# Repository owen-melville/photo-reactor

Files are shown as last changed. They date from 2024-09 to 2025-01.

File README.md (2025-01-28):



<b><h1>Overview:</b></h1>
This repository contains the instructions/code/files for the assembly and operation of the LEDbyXample photoreactor. LEDbyXample is designed for automation and self-driving labs (SDLs), like those at the Acceleration Consortium in Toronto. Although it is designed for 8 mL (2 dram) vials that can be placed inside by a robotic arm with gripper, the 3d-printed design files are easily altered for use with larger vials. Most components, including for the LEDs (~1W to be suitable for photochemistry) are modular and easy to swap.

<b><h2>Authors:</b></h2>

Owen Alfred Melville, Staff Scientist <br>
Monique Ngan, Automation Technician <br>
Jeffrey Watchorn, Staff Scientist <br>
[Acceleration Consortium](https://acceleration.utoronto.ca/) <br>
Last Updated 2024-10-22 <br>

<b><h2>Why LEDbyXample? </b></h2>
<b> Low Cost: </b> Existing photoreactors on the market are quite expensive. One of the cheapest, the [Pioreactor](https://pioreactor.com/en-ca/products/pioreactor-20ml?variant=46984254554168), costs about $340 USD ($460 CAD). There is no need for such a large price. The main parts for the LEDbyXample photoreactor cost about $80 USD, with additional electronic components from kits costing another $80 USD. Many of these additional parts are small electronic components that users may already have, and the kits provide more parts than are required by the reactor. Many of the components could also likely be sourced for cheaper as long as the builders are able to perform their own quality control checks. 

<b> Automation Friendly: </b> LEDbyXample is designed to work with automation and self-driving labs. Vials can be release inside the reactor by a robotic arm with a gripper. Automation of the stirring rpm and LED intensity is controlled through a custom python script and uses a Raspberry Pi Pico which can be commanded through a USB cable. Wireless support for the Pico is available but not documented in this project. 

<b> Skill Development: </b> LEDbyXample is made largely from scratch. This allows builders to develop their DIY skills (3D printing, electronics prototyping, microcontroller use). It contains clear build instructions with photos, links to videos, and clear part lists with links. The Python code used to communicate with the microcontroller is designed to be clear and easily modified. 

<b> Modular / Customizable: </b> LEDbyXample is designed to be modular, with components (LEDs, fans, bases) that can be easily removed or swapped. The 3D printed parts that comprise the physical reactor can be modified to accomodate for different vial sizes. 

<b><h2>Summary of Steps:</b></h2>
  1. Order the required items
  2. 3D Print the required parts
  3. Assemble the photo-reactor
  4. Operate the photo-reactor

<b><h2>Tools Required For This Project:</b></h2>
- [Soldering Iron (for electrical connections)](https://www.amazon.ca/Weller-Soldering-Station-WLACCBSH-02-Silicone/dp/B08MC4HVTR?th=1)
- [Heat Gun (for heat-shrink electrical connections)](https://www.amazon.ca/Mini-Heat-Shrink-Gun-Dual-Temp-dp-B09TYM45BH/dp/B09TYM45BH/ref=dp_ob_title_hi)
- [Wire cutters](https://www.amazon.ca/BOOSDEN-Crafting-Spring-Loaded-Plastics-Clippers/dp/B08ZCHYGN7/?th=1)
- [3D printer](https://ca.store.bambulab.com/products/p1s?srsltid=AfmBOorLX7Ki2ZaYaFx6AWRBcr8wJq_0mTlmHkm-IWXz0sfFRXeNtMNX)

<b><h2>Skills required For This Project: </b></h2>
- Soldering
- Basic Python coding

<b><h1>Step 1: Order the Required Items: </b></h1>

The majority of the components for this project are electronic. 

<b><h2>Materials Required:</b></h2>

These materials are required for the photoreactor. You would need to purchase more to make additional photoreactors. Note, only 1x Fan and 1x Fan Board are strictly needed for stirring. The active cooling Fan and Fan Board are optional. The total cost with 2 LED modules and 1 active cooling (fan) module is $82.80 USD. 

| Item                             | Supplier | Part number                   |Number | Cost (USD) | Total Cost (USD) |
| -------------------------------- | -------- | ----------------------------- | ---------------------------------------------------------------------------------------------------------------------------------------------------------------------------------------------------------------------------------------------------------------------------------------------------------------------------------------------------------------------------------------------------------------------------------------------------------------------------------------------------- | ------ | ----- |
| [Raspberry Pi Pico WH](https://www.pishop.ca/product/raspberry-pi-pico-wh-pre-soldered-headers/  )            | PiShop   | 402-1               |           1      | 9.8   | 9.8        |
| [Grove Shield for Pico](https://www.digikey.ca/en/products/detail/seeed-technology-co-ltd/103100142/13688265?s=N4IgTCBcDaIIwFYCcB2AtHADAZi5uALGGgHIAiIAugL5A)            | Digikey  | 1597-103100142-ND              | 1      | 6.25  | 6.25       |
| [Fan Control Board](https://www.digikey.ca/en/products/detail/adafruit-industries-llc/4808/13590573?s=N4IgTCBcDaIIwFYwA4C0AWZAGNA5AIiALoC%2BQA )               | Digikey  | 1528-4808-ND                   | 2      | 7.99  | 15.98      |
| [Square Fan (20mm Diameter)](https://www.digikey.ca/en/products/detail/cui-devices/CFM-2006CF-060-078-22/19524716?s=N4IgTCBcDa5mBmAtAYQGIFkkAIwAY8A2dJIvHPAdgA4l4kA5AERAF0BfIA)       | Digikey  | 2223-CFM-2006CF-060-078-22-ND |  2      | 11.06 | 22.12      |
| [Grove to Fan Board Connectors](https://www.digikey.ca/en/products/detail/adafruit-industries-llc/4528/11627737?s=N4IgTCBcDaIIwFYwA4C0AWJaByAREAugL5A)   | Digikey  | 1528-4528-ND                  | 2      | 2.83  | 5.66       |
| [Power Barrel Connector](https://www.digikey.ca/en/products/detail/same-sky-formerly-cui-devices/PJ-102AH/408448)     | Digikey  | PJ-102AH                  |  1      | 1.02  | 1.02       |
| [Power Supply](https://www.digikey.ca/en/products/detail/tri-mag-llc/L6R06H-050/7682614)    | Digikey  | L6R06H-050           |  1      | 5.31  | 5.31       |
| [LED Stars (Green)](https://www.digikey.ca/en/products/detail/new-energy/LST1-01H06-GRN1-01/10663110?s=N4IgTCBcDaIDIGUAqBGAtABhQCQwNjQHEAlAOXSxAF0BfIA)               | Digikey  | LST1-01H06-GRN1-01            |  2      | 6.41  | 12.82      |
| [NPN Transistor](https://www.digikey.ca/en/products/detail/nexperia-usa-inc/PZT2222A-115/1158011?s=N4IgTCBcDaIIwHYwILQBYwFYwrigBAHIAiIAugL5A )                  | Digikey  | 1727-4252-1-ND                |  2      | 0.56  | 1.12       |
| [USB Cable for Pico](https://www.digikey.com/en/products/detail/cvilux-usa/DH-20M50056/13177301) |  Digikey | DH-20M50056 | 1 | 2.72 | 2.72 |
| Total Cost (USD) | | | | | <b> $82.80 </b> |
| Total Cost (CAD) | | | | |<b> $115.53 </b> |

<b><h2>Materials Required - Kits:</b></h2>

These materials come in kits, so you may not need them if you already have similar materials. They can be used for multiple reactors or other projects. 

| Item                             | Supplier |  Cost (CAD) |
| -------------------------------- | -------- |  ----- |
| [Prototype PCB Board](https://www.amazon.ca/BOJACK-6-Prototype-Soldering-Compatible-Arduino/dp/B091PZQ4W7/    )              | Amazon Canada        | 21.99 |
| [Nyodenium Magnets 6mm x 2mm](https://www.amazon.ca/Magnets-Refrigertor-Whiteboard-Durable-Multi-Use/dp/B07BJFD6FL/)      | Amazon Canada     | 9.99  |
| [Heat Sinks](https://www.amazon.ca/Awxlumv-Heatsink-25-x25-x10/dp/B08CMK8BMT/ )                       | Amazon Canada   |  10.99 |
| [Resistors](https://www.amazon.ca/Resistor-Assorted-Resistors-Assortment-Experiments/dp/B07L851T3V/?th=1 )                        | Amazon Canada   | 17.99 |
| [Solder Seal Connectors](https://www.amazon.ca/Kuject-Connectors-Waterproof-Electrical-Automotive/dp/B073RMRCC3/) | Amazon Canada   | 16.99 |
| [4-Pin Connectors](https://www.amazon.ca/1-25mm-Connectors-Pre-Crimped-Pixhawk-Silicone/dp/B07S18D3RN/ )  | Amazon Canada           | 21.99 |
| [2-Pin Connectors](https://www.amazon.ca/dp/B00T2U76V0/ref=olp-opf-redir?aod=1&th=1) | Amazon Canada | 10.77 |
| Total Cost (USD) | | <b> $79.29  </b>| 
| Total Cost (CAD) | | <b> $110.71 </b> |

<b><h2>Generic Materials Required</b></h2>
  - Wires (at least red, black, blue, and yellow)
  - Solder
  - Filament for 3D printing (eg [PLA](https://ca.store.bambulab.com/products/pla-basic-filament?gad_source=1&gclid=Cj0KCQjwpP63BhDYARIsAOQkATYc5jM-nciSOOw8pbxHA_WIkh3n5OJYfMMvQm4q8-BjsxyQY5-RIlQaAhdqEALw_wcB) and [ASA](https://ca.store.bambulab.com/products/asa-filament?srsltid=AfmBOor0TaklWc8wcPPxX6YhTCeVZ4l1UiV82qqBd3xhd9iYvP6Alb0c))

<b><h2>Photo of Materials </b></h2>
 <br>

<b><h1>Step 2: 3D Print the Parts: </b></h1>

All the 3D printed parts can be printed with 0.2 mm layer height and a 0.4 mm nozzle. For prototyping or low-temperature reactors, PLA filament can be used. For higher temperatures or shorter wavelength (blue,violet,UV), ASA can be used. Since ASA tends to warp, I recommend using glue stick on the print bed. 

| File Name          | Purpose                  | Printing Considerations      | Number Required         | Customization Potential                 |
| ------------------ | ------------------------ | ---------------------------- | ----------------------- | --------------------------------------- |
| LED_holder.stl     | Holds LED + Heat Sink    | None                         | 1 per LED               |                                         |
| blank_holder.stl   | Blocks Window            | None                         | 1 per unblocked window  |                                         |
| fan_base.stl       | Holds Fan + Magnets      | Tree Supports from base only | 1                       | Change inset for larger fan             |
| fan_holder.stl     | Holds Cooling Fan        | Tree supports from base only | Only if cooling desired |                                         |
| reactor_shield.stl | Holds Vial               | Tree supports from base only | 1                       | Change circle diameter for larger vial  |
| screw_base.stl     | Connects reactor to base | None                         | 1                       | Change screw pattern for different base |



<b><h1>Step 3: Assemble the Photoreactor: </b></h1>

The 3D printed parts are modular. When assembled, they should look like this:



<b><h2> Step 3a: Assemble the LED Holders </b></h2>

The LED Holder takes the 3D printed insert, and adds in a heat sink and a ~1W LED with attached wires to be controlled by the microcontroller. 

<b>Parts Required:</b>
- LED star
- Wires
- 2-Pin Connectors (or alternative)
- 3D Printed LED Holder
- Solder seal connectors
- Heat sinks

<b>Steps:</b>
  1. Take your LED star, it should have two large soldering pads labelled + and -


 
  2. Clean the LED star pads using rubbing alcohol (isopropanol) and a tissue
  3. ***Tricky step Alert*** Attach a red wire to the + labelled pad on the right of the star, and tape it down away from the pad to keep it in place. Heat up your soldering iron in a well ventilated area, then place it over the wire. Using your non-dominant hand, feed solder to the pad from different directions, allowing it to flow onto the pad. Once the solder has covered the whole pad, carefully remove the soldering iron and replace it in its holder. The wire should be encased in solder that has made a strong bind with the pad. If after 2 minutes, gentle pressure on the solder pushes it off the pad, you may need to clean the pad and repeat the process. For tips on this process, see this video (Time Stamp 4:30) https://www.youtube.com/watch?v=H-82av4zQKY&ab_channel=MrTroutDT

https://github.com/user-attachments/assets/7bd34561-cb51-4cb3-8f49-8e8b69328b1f

  4. Repeat the last process using a black wire and the - labelled pad on the right of the star. Ensure the contact has been well made after completion


 
  5. Remove the adhesive from the heat sink, and slide it into the 3D printed LED holder. Note that the spikes of the heat sink point outwards, towards the thinner side. The flat side of the heat sink should point inwards towards the thinner side.
     


  6. Carefully feed the red and black wire through the hole at the bottom of the LED holder. If your wires will not fit, you can use a sharp knife to cut open the channel. As you feed the wires through, you may need to bend them so you can position the LED in a central location on the heat sink.


 
  7. If you wanted a permanent setup, you could wire these red and black ends straight to your LED board (Step 3c). However, to make them removable/swappable, the wires need connectors. I recommend getting a set of pre-wired connectors with red and black wires at the non-connector end. Take the red wire from your LED and the red wire from the connector, and place them in a solder seal connector so that the bare ends of the wires are touching and under the "solder" of the connector. Use your heat gun to carefully heat up the solder seal connector from different angles. First the plastic will melt, sealing the wires together, then you will see the solder spreading from the central area, which should create a proper connection between the two wires. Let the connection cool. To check that the wiring has been made correctly, you can use a multimeter, comparing the LED pad to the appropriate pin in the connector. Use this youtube video for guidance: https://www.youtube.com/watch?v=bvDk3HzS7lM&ab_channel=SkillBuilder


  
  8. Repeat the last step to connect the black wires.

<i>Congratulations, you have created your LED holder, which can slide in and out of the photoreactor! You can create as many of these as you have LEDs that you want to use </i>


 
<b><h2> Step 3b: Assemble the Fan Base </b></h2>

The fan base holds a fan with magnets to allow for magnetic stirring.

<b>Parts Required:</b>
- 3D Printed Fan Base
- Fan
- Wires
- Super glue / double-sided tape
- Magnets (x2)
- 4-Pin Connectors (or alternative)

<b>Steps:</b>
  1. Thread the wires through the hole near the center of the fan base, with the black side of the fan facing up.



  2. Carefully pull on the wires and wiggle the fan into the center square.



  3. Using super glue or double-sided tape, carefully place the magnets on the top of the fan.



  4. <b>Attach the connectors:</b> You can wire the fan to a 4-pin connector using the optional kit or an alternative. 
  
  <i>Using Optional Kit:</i> Using the same technique as in Step 3a - 7, use solder seal connectors to extend the length of the fan wires by attaching them to pre-crimped wires from the electrical connector kit. Then, connect each wire to the connector head. When inserted correctly, the ends of the wire should be fully contained inside the plastic connectors, and fit snugly in place.



  <i>Using Other Connectors:</i> If you have a pre-wired connector with 4 wire leads, you can use that instead of the connector kit. Using the same technique as in Step 3a - 7, use solder seal connectors to connect the fan wires to your pre-wired 4-pin connector. 



<i>Congratulations, you have created your Fan Base which is used to stir a magnetic rod in the reactor </i>

<b><h2> Step 3c: (Optional) Assemble the Fan Holder </b></h2>

The fan holder holds a fan to actively cool the reactor vial. The cooling capacity of the current setup is unknown, and it is possible a larger or a stronger fan is required. This will be investigated for future versions of the photoreactor. 

<b>Parts Required:</b>
- 3D Printed Fan Holder
- Fan
- Wires
- 4-Pin Connectors (or alternative)

<b>Steps:</b>
  1. Thread the wires through the hole near the bottom of the fan holder, with the black side of the fan facing out.



  2. Carefully pull on the wires and pull the fan into its slot.



  3. Using the same technique as in Step 3a - 7, use solder seal connectors to extend the length of the fan wires by attaching them to pre-crimped wires, then carefully insert the pre-crimped wires into the connector head. Alternatively, if you have a pre-wired connector with 4 wire leads, you can use that instead.



<i>Congratulations, you have created your Fan Holder which is used to cool the reactor </i>

<b><h2> Step 3d: Assemble the LED Board </b></h2>

The LED Board uses transistors to control the on/off status of the LEDs, with the signal to the transistor coming from the Rasperry pi. It also has a power inlet port to power the LEDs separately from the Pi, as they draw quite a bit of current. In the future, an LED board could be purchased to directly control the LED, including its intensity, something not currently possible with this design. The design described here controls 2 LEDs at a time, but it could be extended to control more LEDs at once. 

<b>Parts Required:</b>
- PCB board from Kit (60x40 mm)
- Wires
- 1x 1000 Ohm resistor
- 2x 5.6 Ohm resistor
- 2x 390 Ohm resistor
- 2x NPN Transistors
- 4-Pin Connectors (or alternative)
- 2-Pin Connectors (or alternative)
- 1x Power Barrel Connector

<b>Steps:</b>



  1. Mount the power board and solder in a 1000 Ohm resistor between the power and ground sides. This creates a power port. The GND side represents your ground, and 5V your high voltage.
  2. Solder the circuit diagram above. For now, leave the open circles with text labels. The power supply and 1000 Ohm resistor are already completed in step 1. For the NPN transistors, the drawing below shows the schematic. Pin 1 (base) goes to the 330 Ohm resistor, and eventually to the RPi GPIO Pin. This acts like a switch for this LED. Pin 2 (collector) goes towards the LED and the power supply. Pin 3 (emitter) goes to ground.



  3. Solder wires into the open circles that connect to the RPi GPIO pins. The other end of the wire can be bare or an open pin. We will connect these to the RPi in a later step.
  4. Solder wires into the open circles that connect to the LED. For clarity, you can use red wires to go towards the power supply, and black wires towards the transistors. These wires should be at their other end connected to the complementary connectors that you used in Steps 3a-7 and 3a-8. These are meant to connect and disconnect the LED holders so you can change them.
  5. Solder a black wire from the ground/- terminal. The other end of the wire can be bare or an open pin. We will connect this wire to the RPi Ground Pin in a later step, to ensure a common ground.
  

  
  6. (Optional): To add more LED outputs, add more of this section of the circuit diagram, connected in the same way. If you add many more LEDs, you may require a power supply that is rated for higher current. 



<i>Congratulations, you have created your LED Board which is used to control the reactor LEDs</i>

<b><h2> Step 3e: Assemble the Fan Board </b></h2>

The Fan Board uses pre-made fan control boards to control the RPM of the fans. It connects to the Rasperry pi and to a separate power supply. The current design is for 2 fans (1 cooling, 1 stirring) but could be easily be extended for use with more fans. 

<b>Parts Required:</b>
- PCB board (60x40 mm)
- Wires
- 1x 1000 Ohm resistor
- 2x Fan Control Board
- 2x Grove to Fan Board Connectors
- 1x Power Barrel Connector (Optional)

<b>Steps:</b>



  1a. (Optional) Mount the power board and solder in a 1000 Ohm resistor between the power and ground sides. This creates a power port. The GND side represents your ground, and 5V your high voltage.
  1b. Alternatively, you can connect the 5V using a wire to the 5V section of the LED board or to the 5V Pin in the Pico. This means one less power supply, but will draw power either from the LED power supply or from the Pico (which you don't want to draw too much from). 
  2. Solder the circuit diagram above. Solder wires into the open circles for the fan power (red) and ground (black). These will go to the 4-pin connector to the fan.
  3. For each Fan Control Board, solder wires into the "FAN" (blue) and "TACH" (yellow) ports, the other ends will go to the 4-pin connector to the fan.
  4. For each Fan Control Board, attach a Grove to Fan Board Connector. This will connect to the RPi.
  5. Take the power (red), ground (black), tach (yellow), and fan (blue) wires and connect them to a 4-pin connector that complements the one you created for your fans in step 3b-4. 



<i>Congratulations, you have created your Fan Board which is used to control the reactor Fans</i>

<b><h2> Step 3f: Combine the Electronics </b></h2>

We need to connect the boards to the raspberry pi, which controls them. Optionally, you can choose to house them in the 3D printed holder, the parts of which you would need to print. This housing is only to keep the electronics tidy, and is not needed. 

<b>Parts Required:</b>
- Assembled Fan Board (Step 3e)
- Assembled LED Board (Step 3d)
- Raspberry Pi Pico WH
- Grove Shield for Pico
- USB Cable for Pico (USB-A to micro-USB)
- Power Supply (for LED Board)
- (Optional): Power Supply (for Fan Board)
- (Optional): 3D Printed electronics housing

<b>Steps:</b>
  1. Place the Raspberry Pi into the Grove Shield. This requires some force so that it goes in all the way.
  2. Common ground: Take the wires directed towards "RPi Ground" from the Fan and LED Boards and connect them to any open pin on the Raspberry Pi Pico labelled GND.
  3. Signal wires (LEDs): Take the wires directed towards "RPi GPIO Pin 0" and "RPi GPIO Pin 1" from the LED board and connect them to the Raspberry Pi Pico in the corresponding Pins ("GP0" and "GP1")
  4. Signal wires (Fans): Take the Grove-to-stemma connectors from the fan boards and connect them to the top-right corner slots on the Raspberry Pi Pico (with the USB connector oriented up).

 <br>

<b> Optional: Add the electronics to a housing </b>

The electronics housing can be used to house the Raspberry Pi Pico and auxillary electronics. The holders for the auxillary electronics will fit the 60x40 mm PCB boards. They can be printed according to the instructions below. For the material you can use PLA but the snapping mechanism on the snap lid may work better with PETG. 

| File Name                            | Purpose                     | Printing Considerations | Number Required | Customization Potential                  |
| ------------------------------------ | --------------------------- | ----------------------- | --------------- | ---------------------------------------- |
| Pico Holder_MainBody.stl             | Holds the Pico              | Flat side down          | 1               |                                          |
| Pico Holder_Main_Lid.stl             | Lid for Main Unit           | Flat side down          | 1               |                                          |
| Aux_Module.stl                       | Holds LED/Fan Board         | Flat side down          | 2               | Could change to hold different sized PCB |
| Pico Holder_Port_Door_Default.stl    | Blank door for Aux Unit     | Flat side down          | 0               | Can add ports                            |
| Pico Holder_Port_Door_Open_Ports.stl | Custom door for Aux Unit    | Flat side down          | 2               |                                          |
| Pico_Aux_Lid_Snap.stl                | Lid for Aux Unit            | Flat side down          | 2               |                                          |
| Pico Holder_Port_Door_Honeycomb      | Honeycomb door for Aux Unit | Flat side down          | 2               |                                          |

Instructions:
- Print the pieces for the housing
- Place the boards in their respective holders with any connecting wires detached
  
 <br>

- Thread any connecting wires through the honeycomb in the sides
- Attach the side pieces and lids

 <br>

<i> Congratulations, you have finished assembling the electronics! </i>

<b><h2> Step 3g: Assemble the Reactor </b></h2>

<b>Parts Required:</b>
  - Assembled Electronics (Step 3f)
  - Assembled Fan Base (Step 3b)
  - Assembled LED Holder (Step 3a)
  - Assembled Fan Holder (Optional, Step 3c)
  - Reactor Shield
  - Blank Holders (for open unfilled slots)
  - Screw Base (Optional)

<b>Steps:</b>
  1. Connect the electrical connectors for each LED and fan to the electrical setup.

 <br>

  2. Assemble the reactor parts. The LED holder, blank holders, and fan holders should slot easily into the 4 slots on the sides of the reactor shield. The reactor shield slots onto the fan base, which slots onto the screw base. The screw base has slots for fastening the base of the reactor. These could be modified to attach the reactor to a different base or with different screws.

 </br>

<i> Congratulations, you have fully assembled the LEDbyXAmple photoreactor! </i>

<b><h1>Step 4: Operate the Photoreactor: </b></h1>

To operate the photoreactor, we will need to use a Python script that connects to the RPi Pico. The script can be used to control the RPM of the fan (with some constraints) and to turn the LEDs on and off as needed. 

<b><h2> Step 4a: Installations </b></h2>

<b>Steps:</b>
  1. Install a code editor, we recommend VSCode. 
  2. Install Python on your computer if it is not already installed.
  3. Install Micropico extension in VScode
  4. Connect the RPi Pico to your computer using the Usb B Micro B to Usb A Cable, while pressing the BOOTSEL button on the Pico. A file directory for the Pico should show up in your file explorer.
  5. Flash the Raspberry Pi  by downloading the [MicroPython UF2 file for Pico W](https://www.raspberrypi.com/documentation/microcontrollers/micropython.html) into your computer and moving the file to the directory of the Raspberry Pi. The file directory should disappear after this and disconnect it from your computer.
  6. Open a new “micropico vPERL” terminal in VS code
  7. When the Raspberry Pi is connected it should show a success message in green text.

VS Code - Raspberry Pi Connected

<b><h2> Step 4b: Python Scripts </b></h2>

<b>Steps:</b>
  1. Download the python scripts from this github repository, including photo_reactor.py and reactor_test.py and the "lib" folder with the drivers for the fan boards
  2. In VSCode, “Configure project” for the folder that contains the lib folder, photo_reactor.py & reactor_test.py files
  3. Upload the project to Raspberry Pi by right clicking on folder containing all the project files & select  “Upload project to Pico”
  4. To run the test code, select reactor_test.py file & right click to choose “Run current file on Pico”

<b> NOTE: Do not look directly at your LEDs! We recommend using blue-light blocking glasses and never looking directly at the emitted light </b>
	
<b><h2> Step 4b: Operation </h2></b>

The LEDbyXample photoreactor currently has two functions: Switch on/off the LEDs (could have up to 4 in one reactor) and initialize/set the rpm of the fans (both for stirring and cooling). 

<b>Functions:</b>
  1. <b> add_fan ( fan ) </b> takes in the SoftI2C address with two pins that are associated with controlling the fan, these numbers will change depending on which slot you put your fans in on the pico board
  2. <b> add_led ( pin ) </b> takes in the GPIO pin number for a specific LED to set it up for operation
  3. <b> turn_on_led ( index ) </b> turns on the LED with the specified index
  4. <b> turn_off_led ( index ) </b> turns off the LED with the specified index
  5. <b> set_led_brightness (index, duty_cycle) </b> Set the brightness of an LED to between 0 and 100 (duty_cycle) using pulse width modulation.
  6. <b> initialize_fan ( index, starting_duty_cycle) </b> attempts to turn on fan with specific index, it will try different duty cycles until it is able to measure an rpm (sometimes the initial duty cycle is insufficient when there is a load like a stir bar in a thick liquid. Note that the fan may not initialize if the stir bar is too close or too far away from the magnets. This matters more if you are using a different vial than the 2 dram (8 mL) vial this reactor was designed for. This function returns the duty cycle that was sufficient to activate the fan. 
  7. <b> set_fan_rpm (index, target_rpm, duty_cycle) </b> This attempts to get the specified fan to reach a specific rpm, starting with the specified duty cycle. It may not maintain that rpm, but will keep the same duty cycle, which is returned by the function.
  8. <b> hold_fan_rpm (index, target_rpm, target_time, duty cycle) </b> This attempts to adjust the input duty cycle to maintain a target rpm for a specific time period. This means adjusting the duty cycle up and down slightly as needed. 

<b><h1> Future Steps </b></h1>

1. Increase the physical robustnest of the design, preventing the pieces from falling over when wires are tugged.
2. Measure the temperature of the reactor using a thermocouple or an IR probe/camera.
3. Measure the spatial uniformity of the LED emission in the reactor.
4. Use feedback control to increase cooling fan speed when temperature rises. This might require a stronger cooling fan.

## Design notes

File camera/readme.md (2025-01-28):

<h1>Imaging Module:</h1>

_Camera_cropped

The following describes how to turn the photoreactor into an imaging reactor. 

<h2> Parts Needed: </h2>

[Camera](https://www.digikey.ca/en/products/detail/adafruit-industries-llc/5733/21839820)

[USB Extender](https://www.amazon.ca/UGREEN-Extension-Extender-Transfer-Playstation/dp/B00P0ES0VC/ref=sr_1_5?crid=3N7RB1UZNDPM9&dib=eyJ2IjoiMSJ9.BhVm3nQeHf4O2F3fpluVa9MnVuqOXOqPzwndRqhN5wIk5KDBnGOyOacnbayJ5clOGYHaLHxdhKI6rnkZir4PwAJsOd09U1QD9qv1fTuxgMCQPkcKCM6-ybV8UKALXnw_wskcogvQg65o7bOX424w-_h-Qt9qaEt4mN6ElmxiGWEC7KLLOdewoQaJxE13Zu6O2pco-PesKyHwSwAnMI3XakVCboK7iKjdPY2Hb6xurQVthA3WPzighLCuuS8IEw0yXjPTXVnI_6q1riQLdB_S-qeTKg8rih4-pd0e4aAKv7cEObw2ZyZiPoslMgMZFGMUNWv4swpIfWzd6cllzPrXc40BNtEXacHGO-ZcmUbCqNeN4LvlyVmxF8kmsnndf9YWSJOVJwtSmoHuiI7UzX6fD9ZlHBly3g4CTy-M4vVkOYIF1IITzI5kdRMVn7tppYce.ysUtx2_TLXXK0cOXU83ke25pdNLNYkddpoul-cmYRAo&dib_tag=se&keywords=usb%2Bextender&qid=1737577841&sprefix=usb%2Bextender%2Caps%2C96&sr=8-5&th=1)

<i>Note: The USB extender does seem to create issues with the camera in some instances. It may be an issue with power that can be solved with a shorter cable or with an actively-powered USB hub. I am also looking into using other cameras that may work better for this application. </i>

<h2> 3D Printed Parts: </h2>

- <b>Camera_Module:</b> This holds the camera. Flip 180 degrees and print with supports.
- <b>Camera_Spacer:</b> This can be placed under the tunnel to prevent the reactor from tipping. No supports needed for printing.
- <b>Camera_Tunnel_Lower:</b> This distances the camera from the vial and slides into the side of the reactor. No supports needed for printing.
- <b>Camera_Tunnel_Upper:</b> This slides onto the top of the camera tunnel to block out light. The connection isn't that robust and could be improved. No supports needed for printing. 

<i>There are longer and shorter versions of the tunnel here. I'm not certain what the best length is for the tunnel for image quality.</i>

<h2> Assembly: </h2>
1. Attach the camera onto the camera module using the adhesive tape attached to the camera. 

1000009149-removebg-preview (1)

2. Slot the camera module in at the edge of the tunnel.

1000009152-removebg-preview (1)

3. Slide the tunnel cover onto the top of the tunnel.

1000009151-removebg-preview (1)

4. Slot the tunnel onto the photoreactor. Place the camera spacer below the tunnel if you want to provide counter support.

_Camera_cropped

<h2>Lighting: </h2>

I used white [LED stars](https://www.digikey.com/en/products/detail/new-energy/LST1-01H06-3080-01/10663115) in the photo-reactor, and slid in a 0.3 mm white sheet between the reactor and the module to diffuse the light. This does create some glare. This could be improved. Other light sources (not LED stars) could be used. 

reactor_image

<h2> Operation & Code: </h2>

All these programs were written by ChatGPT and I edited them. <b>camera_index</b> depends on the number of cameras you have on your computer. You can check your device manager but if you have a built-in cam its usually "1" otherwise its "0". You should "pip install opencv-python" or equivalent prior to running these in your python environment (virtual is fine). I had trouble installing this in older Python environments, so make sure its a newer version. 

 - <b>record_video.py</b> you can monitor the reactor and hit buttons to record (this could be more automated to be timed for before and after the material is dripped in). 

 - <b>take_image.py</b> you can take snapshots and save them

 - <b>monitor_video.py</b> you can simply watch the video feed with this, nothing is recorded

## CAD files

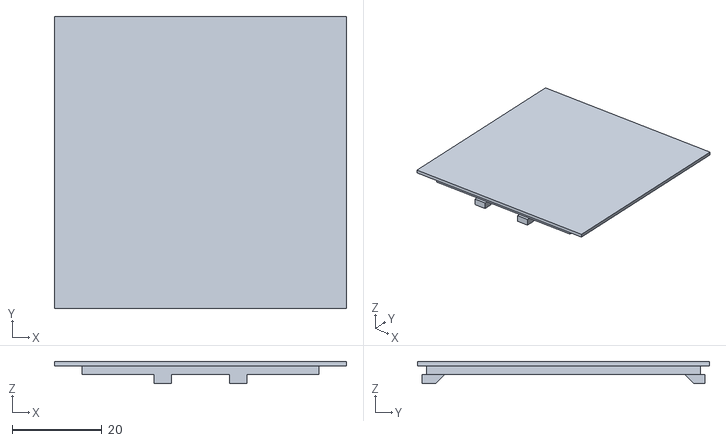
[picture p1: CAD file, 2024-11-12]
3D_Printed_Parts/electronics_casing/Snap_Lid_Pico_Main.stl
65.0 x 65.0 x 5.00

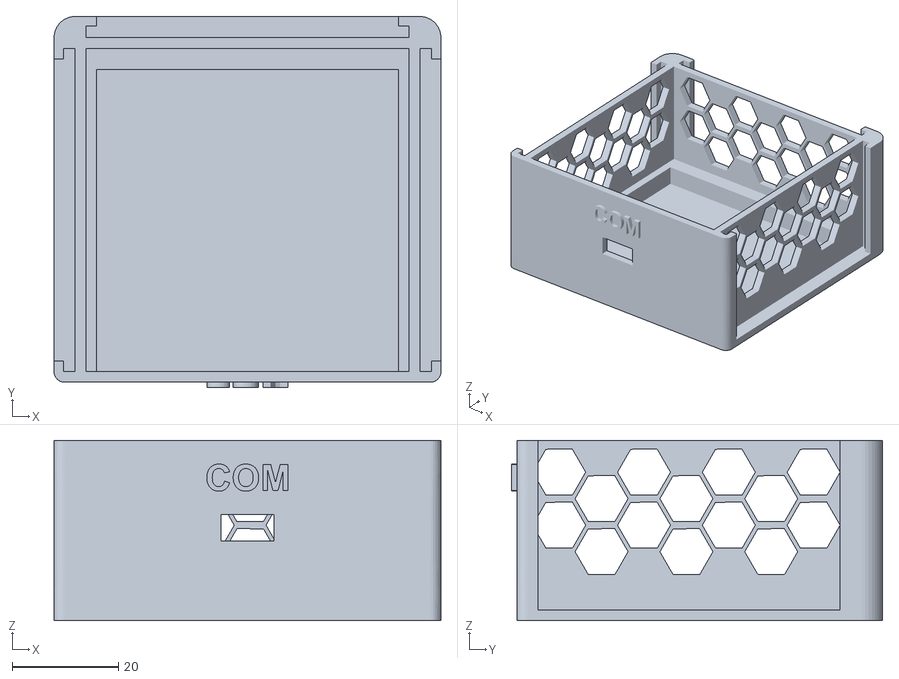
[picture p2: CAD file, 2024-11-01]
3D_Printed_Parts/electronics_casing/Pico Holder_MainBody.stl
73.0 x 70.0 x 34.0

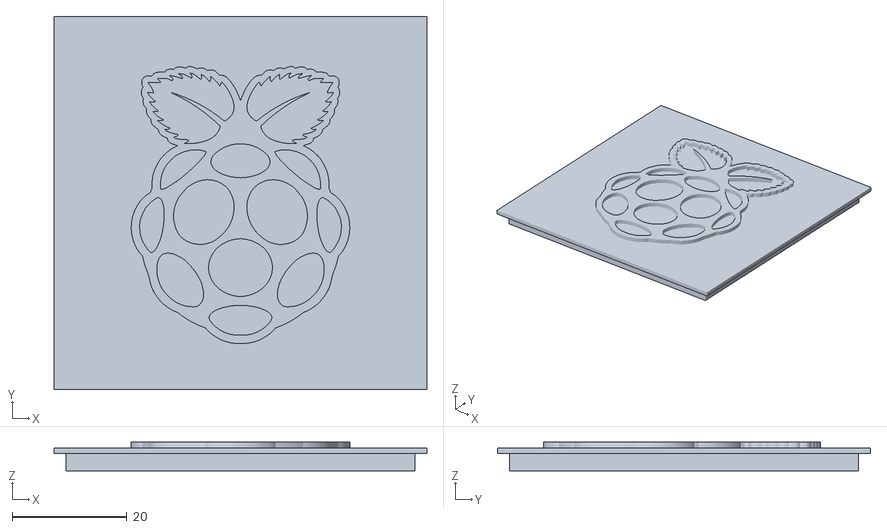
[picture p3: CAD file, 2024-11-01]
3D_Printed_Parts/electronics_casing/Pico Holder_Main_Lid.stl
65.0 x 65.0 x 5.00

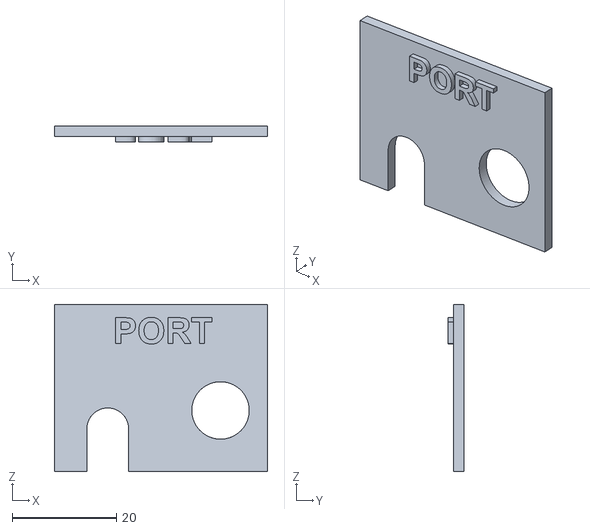
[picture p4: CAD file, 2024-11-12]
3D_Printed_Parts/electronics_casing/Pico Holder_Port_Door_Open_Ports.stl
40.8 x 3.00 x 32.0

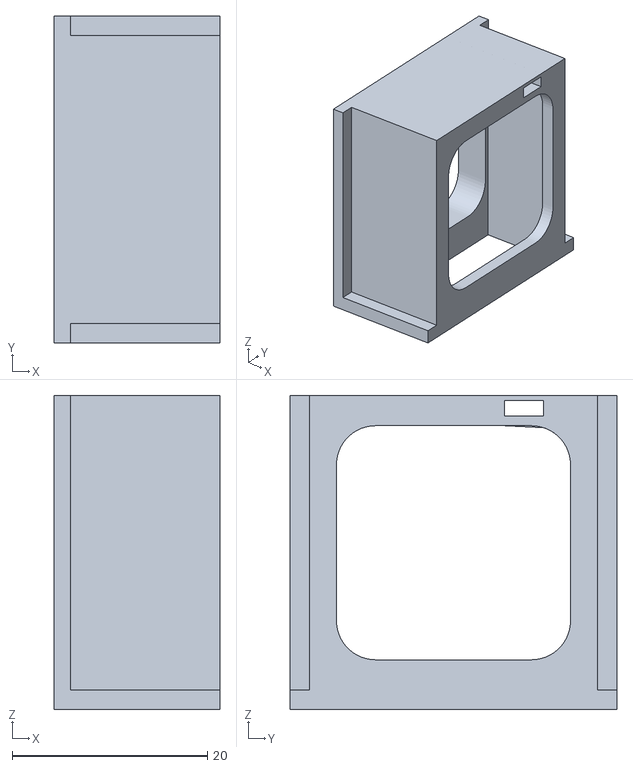
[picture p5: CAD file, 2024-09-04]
3D_Printed_Parts/LED_holder.stl
17.0 x 33.5 x 32.2

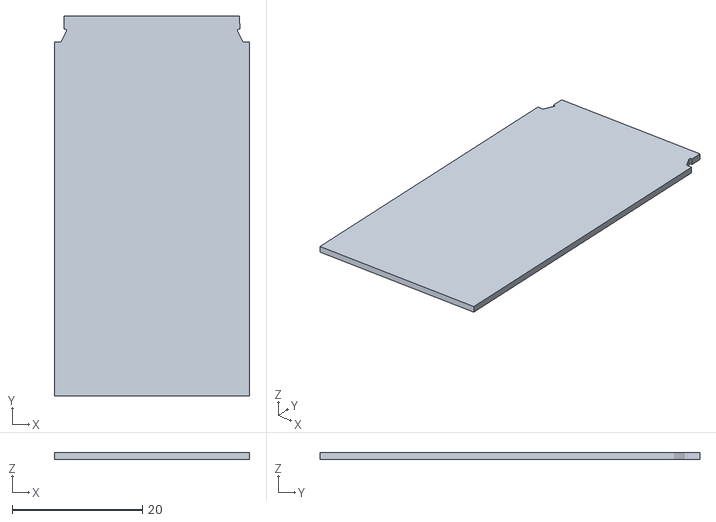
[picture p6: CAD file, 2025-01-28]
camera/camera_tunnel_upper.stl
30.0 x 58.4 x 1.00

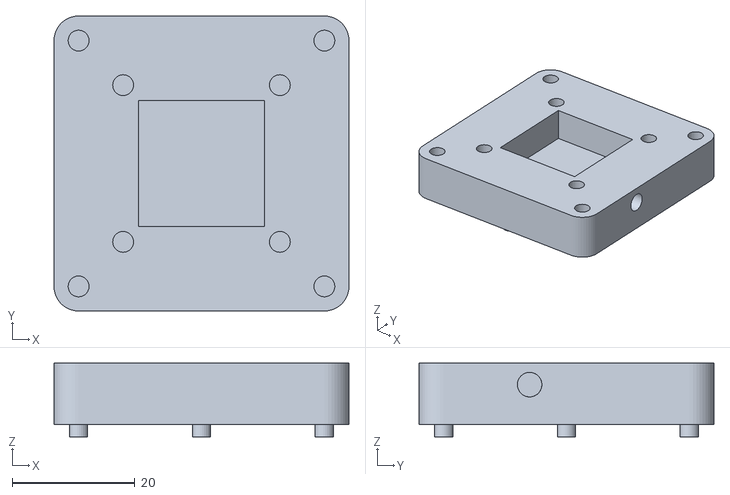
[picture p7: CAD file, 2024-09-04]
3D_Printed_Parts/fan_base.stl
48.0 x 48.0 x 12.0

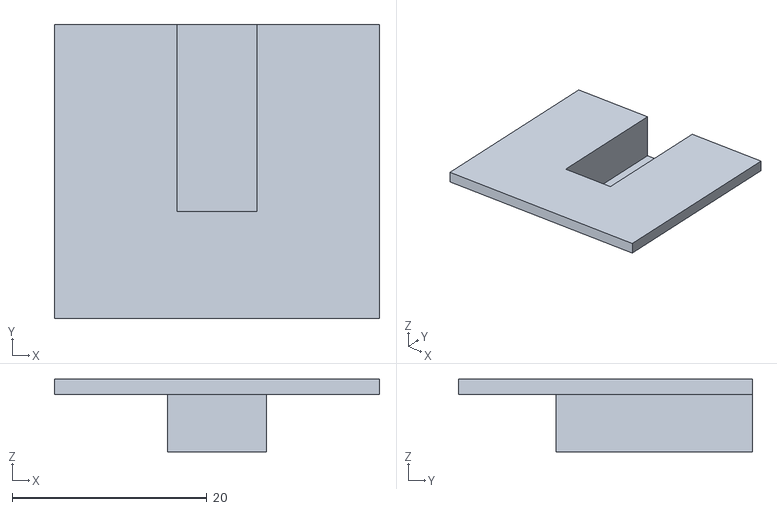
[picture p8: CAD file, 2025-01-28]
camera/camera_module.stl
33.4 x 30.2 x 7.50

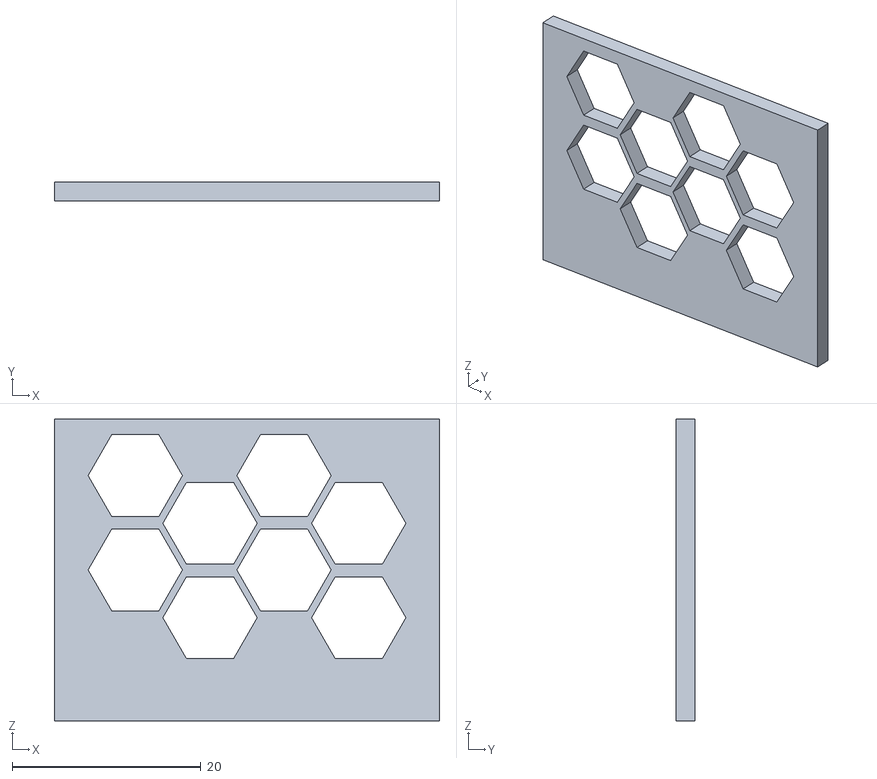
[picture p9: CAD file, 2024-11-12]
3D_Printed_Parts/electronics_casing/Pico Holder_Port_Door_Honeycomb.stl
40.8 x 2.00 x 32.0

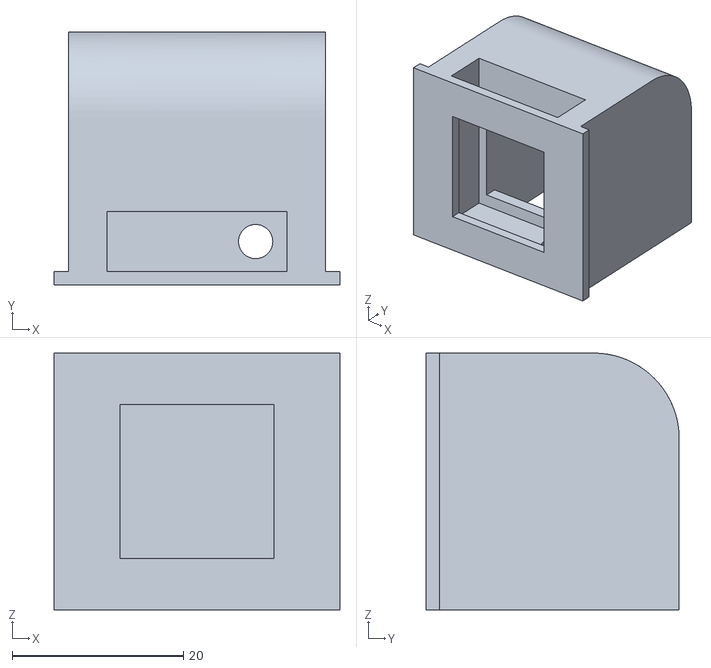
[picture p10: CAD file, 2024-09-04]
3D_Printed_Parts/fan_holder.stl
33.4 x 29.6 x 30.0

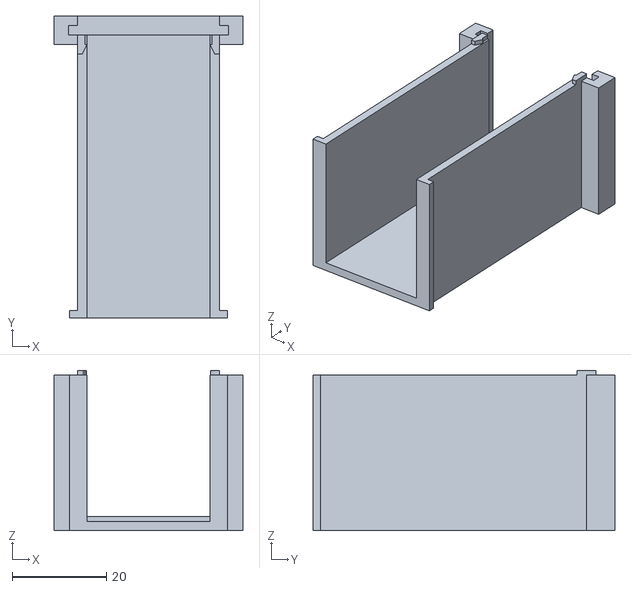
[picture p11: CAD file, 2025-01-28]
camera/camera_tunnel_lower.stl
40.0 x 64.0 x 34.0

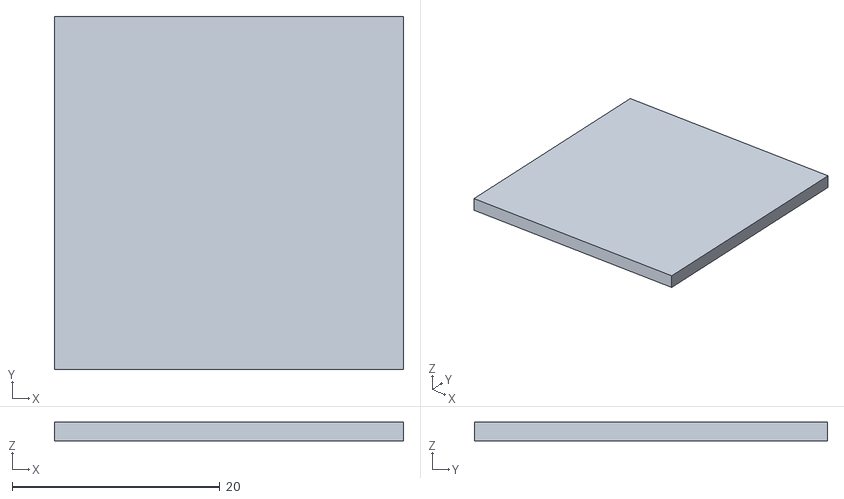
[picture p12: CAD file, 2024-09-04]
3D_Printed_Parts/blank_holder.stl
33.6 x 34.0 x 1.80

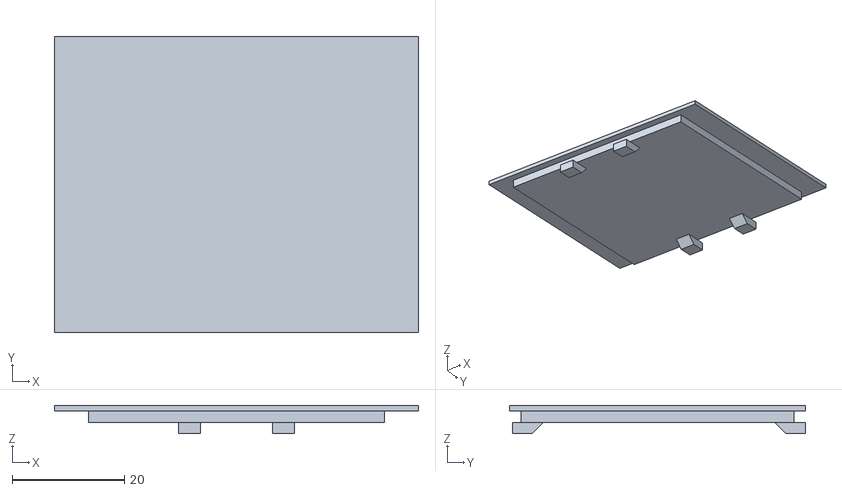
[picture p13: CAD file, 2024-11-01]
3D_Printed_Parts/electronics_casing/Pico_Aux_Lid_Snap.stl
65.0 x 52.8 x 5.00

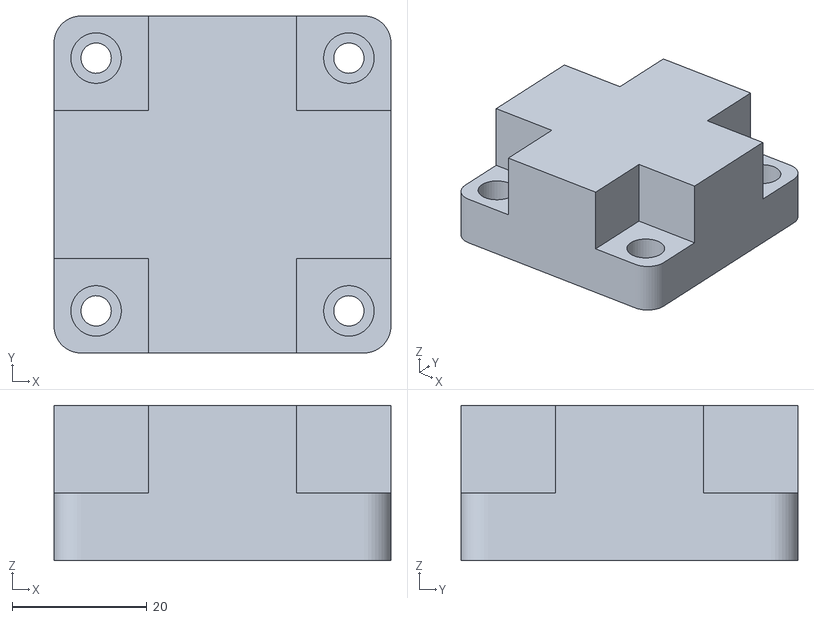
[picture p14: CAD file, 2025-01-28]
camera/camera_spacer.stl
50.0 x 50.0 x 23.0

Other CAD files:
3D_Printed_Parts/reactor_shield.stl
camera/camera_tunnel_upper_extended.stl
3D_Printed_Parts/electronics_casing/Pico Holder_Port_Door_Default.stl
camera/camera_tunnel_lower_extended.stl
3D_Printed_Parts/Base_North v3.f3d
3D_Printed_Parts/Fan Holder v4.f3d
3D_Printed_Parts/Fan_Base_New v6.f3d
3D_Printed_Parts/LED Holder 25x25 heat sink v3.f3d
3D_Printed_Parts/Reactor_Shield v6.f3d
3D_Printed_Parts/electronics_casing/Aux_Module.f3d
3D_Printed_Parts/electronics_casing/Aux_Module.stl
3D_Printed_Parts/electronics_casing/Pico Holder_MainBody.f3d
3D_Printed_Parts/electronics_casing/Pico Holder_Main_Lid.f3d
3D_Printed_Parts/electronics_casing/Pico Holder_Port_Door_Default.f3d
3D_Printed_Parts/electronics_casing/Pico_Aux_Lid_Snap.f3d
3D_Printed_Parts/screw_base.stl

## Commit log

2024-10-03 Rename Base_North v3.stl to screw_base.stl
    [screw_base.stl]
2024-10-03 Rename Reactor_Shield v4.stl to reactor_shield.stl
    [reactor_shield.stl]
2024-10-03 Rename LED Holder 25x25 heat sink v4.stl to LED_holder.stl
    [LED_holder.stl]
2024-10-03 Rename Fan_Base_New v6.stl to fan_base.stl
    [fan_base.stl]
2024-10-03 Rename Fan Holder v1.stl to fan_holder.stl
    [fan_holder.stl]
2024-10-03 Rename Blank_Holder v2.stl to blank_holder.stl
    [blank_holder.stl]
2024-11-01 added casing and code updates
    [Pico Holder_MainBody v2.f3d, Pico Holder_MainBody v2.stl, Pico Holder_Main_Lid v4.f3d, Pico Holder_Main_Lid v4.stl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]
2024-11-01 f3d files
    [Base_North v3.f3d, Fan Holder v4.f3d, Fan_Base_New v6.f3d, LED Holder 25x25 heat sink v3.f3d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]
2024-11-12 update files
    [Aux_Module.f3d, Aux_Module.stl, Pico Holder_MainBody.f3d, Pico Holder_MainBody.stl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]
2025-01-22 Rename camera_module v2.stl to camera_module.stl
    [camera_module.stl]
2025-01-22 Rename camera_tunnel_2cm_ext v1.stl to camera_tunnel_lower_extended.stl
    [camera_tunnel_lower_extended.stl]
2025-01-22 Rename camera_tunnel_2cm_ext v1_top.stl to camera_tunnel_upper_extended.stl
    [camera_tunnel_upper_extended.stl]
2025-01-22 Rename camera_spacer v2.stl to camera_spacer.stl
    [camera_spacer.stl]
